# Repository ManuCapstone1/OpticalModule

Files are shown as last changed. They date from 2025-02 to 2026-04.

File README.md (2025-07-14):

# OpticalModule

This Github repository is for storing all pertinent information regarding the functionality and design of the optical module.

<p align="center">
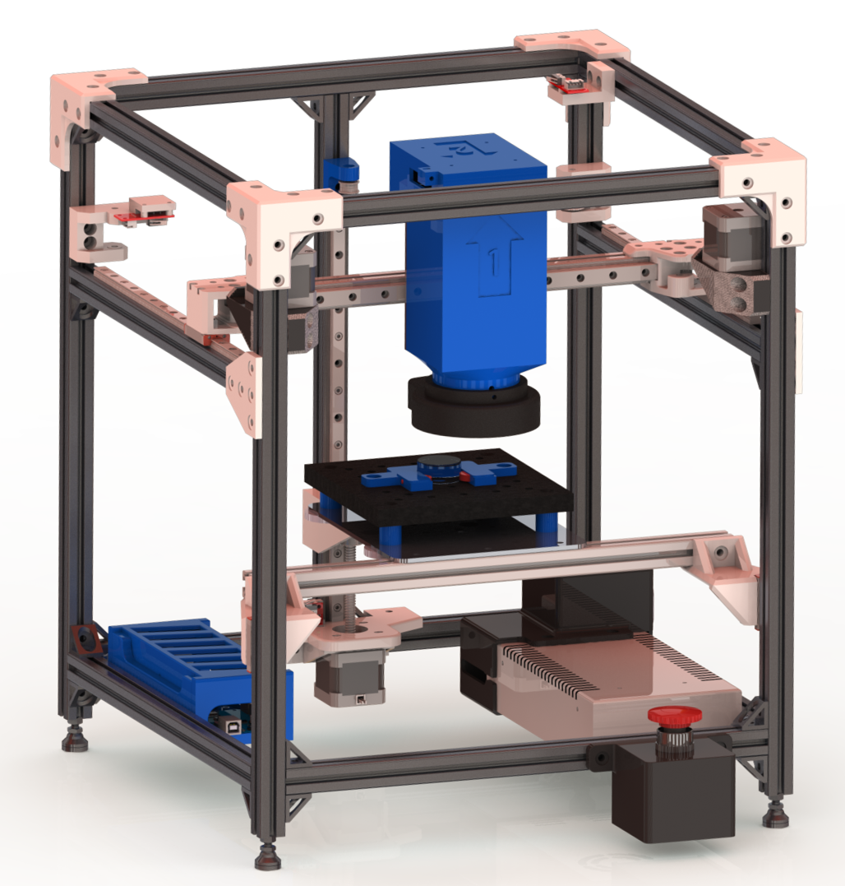
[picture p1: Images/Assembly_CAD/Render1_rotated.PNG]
  
</p>

<p align="center">
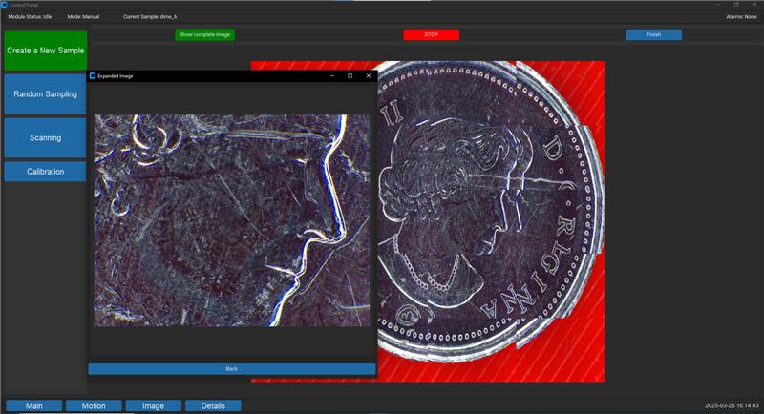
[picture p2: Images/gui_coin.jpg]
  
</p>

---

The [CAD folder](CAD/) has the full assembly of the optical module, along with files for all the 3D printed parts and engineering drawings for machined parts

The [Programming folder](Programming%20Files/) has all the programming files for the project. [pc_files](Programming%20Files/pc_files) has all python files to be run on a windows PC, to interact with the Raspberry Pi with a GUI. [module_program](Programming%20Files/module_program) has all the files to be run on the Raspberry Pi. Keep in mind that file paths are hardcoded, and would need to be modified on new devices.

[Images](Images/) holds images of various aspects of the project. Flowcharts, sample images, and images of the physical product.

[Documentation](Documentation/) lists documents relating to design, use and assembly (e.g. BOM, manual).

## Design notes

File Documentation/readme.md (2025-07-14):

## BOM
File [BOM_OpticalModule](BOM_OpticalModule.xlsx) has a list of all the parts and tools needed to create the optical module, along with links to vendors and parts.

The first sheet has the exhaustive list of all the parts. The second sheet 'Fasteners' has three seperate tables, with various grouping combination for ease of use. The third sheet has a list of all the 3D printed parts and approximate material costs. The fourth sheet has a list of all needed tools to assembly and construct the microscope.

Parts were sourced through the following vendors: Aliexpress, Amazon, piShop, and McMaster. A very rough estimate of all the costs is about $1600 CAD, excluding tax, shipping costs, and tools.

## Assembly Instructions
Instructions on how to assemble and setup all components of the optical module.

## Manual
Instructions on how to run, operate, and maintain the optical module. Does not include design decisions, or assembly instructions.

## Electrical Diagram
Fritzing file of the module's electrical setup.

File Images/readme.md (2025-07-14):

### Assembly_CAD
Rendered images of microscope in CAD from different angles and viewpoints.

### Charuco
Images of charuco board taken with the microscope during testing.

### Diagrams
Flowcharts and diagrams to explain programming structure. Referenced in readme.md file in programming folders.

### Picture
Pictures taken of the microscope from various different angles and viewpoints to assist with assembly.

### coin_stitched_example
An example of the files that would be outputted during a scanning routine of the optical module.

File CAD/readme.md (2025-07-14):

-To access the project assembly to go the "Optical Module Final Assembly" folder and download "Optical Module CAD.zip". 

-Open the "430 Main project assy" file for the final assembly.

The structure of the assmebly for this project took a lot of inspiration from rolohuan's SimpleCore 3D printer.

“rolohaun/SimpleCore: DIY CoreXY Printer called SimpleCore.” https://github.com/rolohaun/SimpleCore/tree/main (accessed Nov. 25, 2024).

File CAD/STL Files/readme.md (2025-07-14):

# 3D Printing Instructions

## Parts List
All .STL files to be 3D printed. Below is the list of all the parts and the quantity needed.
See [Download BOM.xlsx](./OpticalModule/Documentation/Github_BOM.xlsx) for a more detailed BOM.

| Part Name                | Notes                                | Quantity | Link |
|--------------------------|--------------------------------------|----------|------|
| *Enclosure Base V2       |                                      | 1        |      |
| Enclosure Cover Front    |                                      | 1        |      |
| Enclosure Cover Upper    |                                      | 1        |      |
| Belt Adapter             |                                      | 1        |      |
| Idler Mount B            |                                      | 1        |      |
| Idler Mount A            | Limit switch mount                   | 1        |      |
| **XY Motor mount         | One as is, the other mirrored.       | 2        |      |
| **Z Carriage             | One as is, the other mirrored.       | 2        |      |
| Ball Screw Bracket       |                                      | 1        |      |
| Belt Tensioner           |                                      | 1        |      |
| Z Motor bracket          |                                      | 1        |      |
| Left Y Carriage Top      |                                      | 1        | [rolohaun](https://github.com/rolohaun/SimpleCore/tree/main/CAD) | 
| Left Y Carriage Bottom   |                                      | 1        | [rolohaun](https://github.com/rolohaun/SimpleCore/tree/main/CAD) |
| Right Y Carriage Top     |                                      | 1        | [rolohaun](https://github.com/rolohaun/SimpleCore/tree/main/CAD) |
| Right Y Carriage Bottom  |                                      | 1        | [rolohaun](https://github.com/rolohaun/SimpleCore/tree/main/CAD) |
| X Limit Switch Mount     |                                      | 1        |       |
| Housing Top              |                                      | 1        |       |
| Housing Base             |                                      | 1        |       |
| estop enclosure top      |                                      | 1        |       |
| estop enclosure bottom   |                                      | 1        |       |
| Power supply housing     |                                      | 1        |       |
| Sample holder base       |                                      | 1        |       |
| Sample holder clamping plate |                                  | 2        |       |
| Sample holder pin        |   Add a spring from a pen to the cylindrical part of the pin.  | 2        |       |
| ***MGN9 Linear Rail Jig  |  Print standard/weaker settings.     | 2        | [Thingiverse](https://www.thingiverse.com/thing:5903898/files) |
| ***MGN12 Linear Rail Jig |  Print standard/weaker settings.     | 2        | [Thingiverse](https://www.thingiverse.com/thing:5903898/files) |
| T-bracket                |                                      | 4        | [Thingiverse](https://www.thingiverse.com/thing:2503622/files) |
| Top Corner Bracket       |                                      | 4        | [Thingiverse](https://www.thingiverse.com/thing:2655498) |
| Ball Screw Knob          | Scaled at 97%                        | 1        | [Thingiverse](https://www.thingiverse.com/thing:3014508/files) |
| Cable Management Clips   | File not uploaded. Select as needed. | ~10      | [Thingiverse](https://www.thingiverse.com/thing:4612080/files) |

**EnclosureBase should be printed with the supports filling in the interior of the shell.*

** *Print one as is, then print another but mirrored.*

*** *Since these parts are not apart of the ovedrall structure and used just for alignment, they can be printed on weak/low settings (e.g. infill 20%, shell thickness 0.8mm).*

## Recommended Print Settings
### Printer

Recommend using an *FDM printer*. Parts should hold good structural integrity to reduce wear and vibrations of the system.

### Material
Strong materials like ABS are the most preferred. However, PLA and PLA + are sufficient.

### Slicer Setting
The following suggestions are simply *suggestions*. If you are familiar with 3D printing, use you're discretion.

| Parameter        | Suggested Setting |
| -----------------| ----------------- |
| Resolution       | 0.02 mm           |
| Infill           | 40%-60%           |
| Infill Pattern   | Cubic             |
| Shell Thickness  | 1.2 mm            |
| Supports         | > 45 degrees. For nicer surface finish, place supports at the bottom of parts. |

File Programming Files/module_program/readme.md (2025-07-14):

# Overview
The purpose of this code is to operate the physical system. It can receive commands from the GUI and execute the requested method while publishing data on the current module status.

<p align="center">
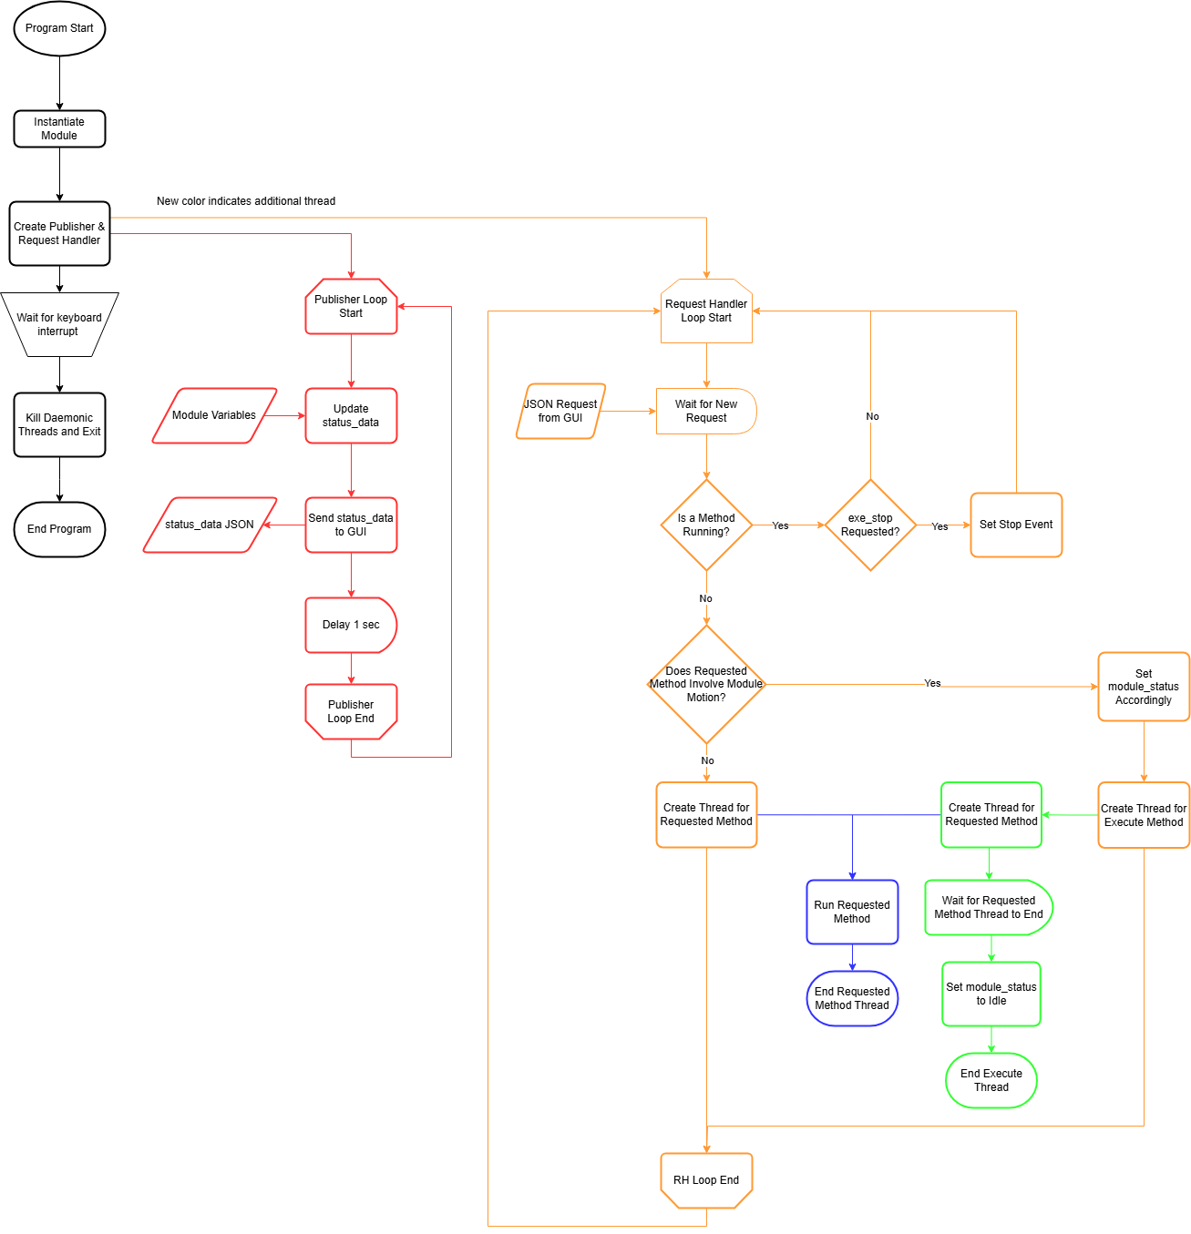
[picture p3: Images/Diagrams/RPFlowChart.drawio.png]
Raspberry Pi Program Diagram
  
</p>

---
# Files

## opticalmodule.py
This Python file contains classes that represent the physical system with methods for system operation.

## rpmain.py
This Python file handles opening and closing sockets and functions for publishing data and handling requests from the GUI.

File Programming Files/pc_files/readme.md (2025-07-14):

# Overview
The purpose of this code is to communicate user requests to the Optical module code (i.e. Raspberry Pi). User requests are handled in a Graphical User Interface (GUI).
The code is designed to be run on a Windows PC that is connected to the Raspberry Pi with an Ethernet cable.

<p align="center">
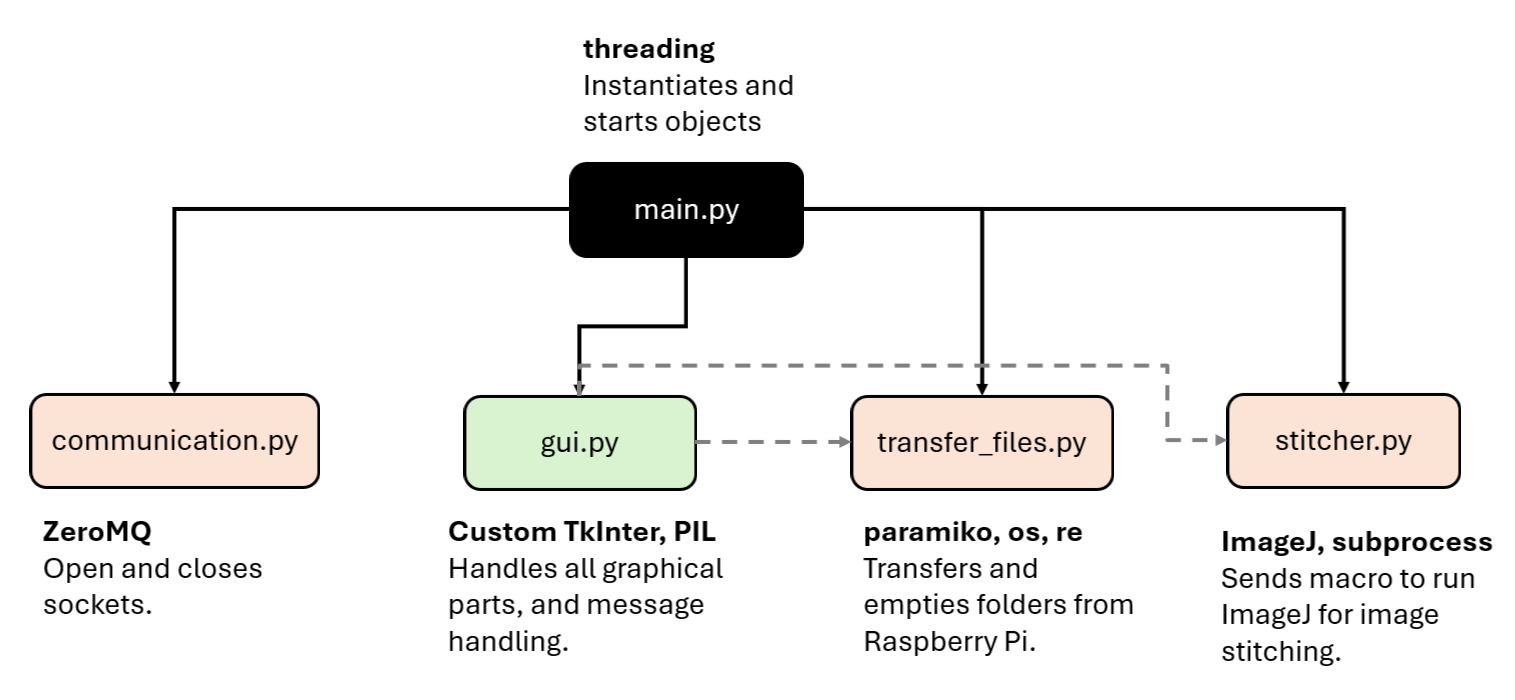
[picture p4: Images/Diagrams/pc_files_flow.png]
PC files diagram
  
</p>

---
# Files

## main.py
All the Python files for the PC, except for main, are simply classes. Main instantiates objects from the other Python files and then starts the program. It also assists with closing the sockets and the program smoothly when the GUI exits.

## communication.py
This Python file handles opening and closing sockets. The Python library to handle the sockets is ZeroMQ. There are two sockets used:

**SUB Socket**
The subscriber socket works in tandem with the Raspberry Pi's publisher socket. The Raspberry Pi sends live data to the PC every second.
This is run on a separate thread so that it can continue to get updates asynchronously.

**REQ Socket**
The request socket works in tandem with the Raspberry Pi's response socket. This is used to send JSON objects to the Raspberry Pi to detail user requests (e.g. exe_stop, number of sampling images).

**Note**
The IP address, host name, and password are hardcoded into the code. Change as needed to fit the specs of your Raspberry Pi or whichever device you use.

<p align="center">
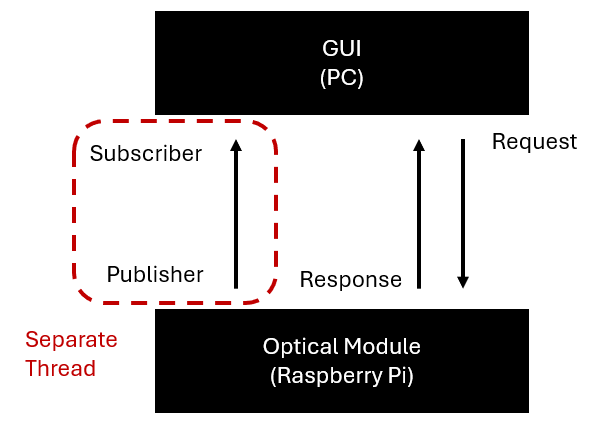
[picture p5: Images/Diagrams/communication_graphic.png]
PC files diagram
  
</p>

## stitcher.py
The stitcher program runs a macro that passes in arguments to ImageJ (i.e. FiJi). The image stitching process takes some time (up to 2 minutes). Therefore, this process is also run on a separate thread when it is called.

## transfer_files.py
Images are stored in a folder on the Raspberry Pi called "image_buffer," regardless of the process being executed. An SFTP client connection must be opened in order to transfer those files from a directory in the Raspberry Pi over to a directory in the PC. Furthermore, to empty the "image_buffer" folder, an SSH client connection is created and then closed after completion. This Python file handles all this communication and connections.

## gui.py
gui.py is basically the "main" code, as it handles all the graphical parts of the GUI, as well as uses the objects from the other files to communicate and sequence the user requests to the Raspberry Pi.
The code can be separated into three main chunks, in order of how it was written: instantiation of variables, graphical components, message handling with the Raspberry Pi.

### Instantiation
At the top of the program, many variables are instantiated. Without some of these instantiations, errors may arise as some variables are updated every second from the Raspberry Pi, but would otherwise only be instantiated if that particular screen where the variable is displayed is open.

Note that it is in this section where the folder paths are instantiated. Change these directories as needed to match your directory.

### Graphics
Most of the code is simply widgets, frames, buttons, etc. to display the GUI. Key functionality to note is that many of the buttons use functions that send data to the Raspberry Pi. For example, the section of code that programs the "Stop" button will also have the code that sends the command to the Raspberry Pi.

### Communication
This section of code includes the image transferring (i.e., using transfer_files.py), code for starting the stitching thread, and the step-by-step processes for handling scanning and sampling processes. There are two key functions I want to note:

**update_status_data**

This function is run every second on a separate thread as it is used in the CommunicationHandler object. This function is run every second, so to ensure thread safety, only unpacking JSON data should be completed here, and everything else should be completed on the main thread.

**update_gui_elements**

This function is called within the update_status_data function like so:

`self.content_frame.after(0, self.update_gui_elements)`

This ensures all actions that need to take place in response to the Raspberry Pi's live data should happen here. This is where significant updates are coded, as well as the "state machine"-like code for running scanning and sampling.
Note that anything that takes more than ~1 second will cause the code to crash, as the function is called every second. Therefore, for any functions that require more time, run that function on a separate thread. For example, this is done for stitching as well as transferring the files from the Raspberry Pi.

---
# In Progress
## Calibration Routine
The platform and camera are leveled and aligned manually. To "calibrate" the camera should return focus score at each corner of the platform to assist the user in knowing what to level/adjust.

## Starting Raspberry Pi Remotely
Currently, there is code in main.py (i.e., run_rpi_python_file function) that can successfully start the Raspberry Pi upon running main.py on the PC. However, there is not any code yet that will close the sockets on the Raspberry Pi when the GUI closes, like there is in main.py. This needs to be completed before run_rpi_python_file should be uncommented.

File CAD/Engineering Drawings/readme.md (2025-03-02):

# Engineering Drawings 

| Part Name                | Notes                     | Quantity  |
|--------------------------|---------------------------|-----------|
| 430 Main project assy    | Full assembly             | 1         |
| Enclosure Backplate      | Metal Backplate for Carriage Enclosure| 1        |
| breadboard platform      | Extra leveling holes in breadboard    | 1         |
| support platform         |                           | 1         |

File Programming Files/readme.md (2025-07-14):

### archived
Folder with old programming files. Many including test files and demos used during the software development process.

### module_program
All the programming files needed and run on the Raspberry Pi. To start the process, run rpmain.py.

### pc_files
All the programming files needed to run a GUI on a windows PC. To start the process, run main.py.

### fiji
Files and information pertaining to Fiji (ImageJ), which handles the image stitching.

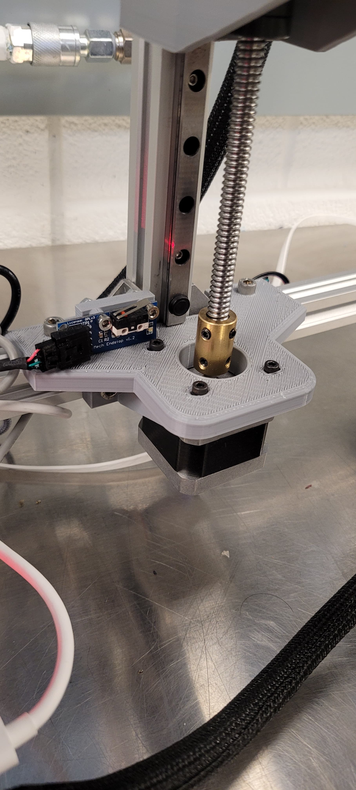
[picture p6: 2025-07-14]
Images/Picture/z_bracket.jpg

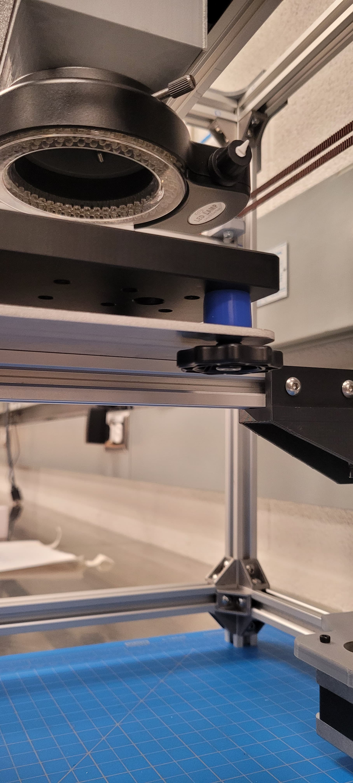
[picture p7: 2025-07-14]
Images/Picture/platform_underside.jpg

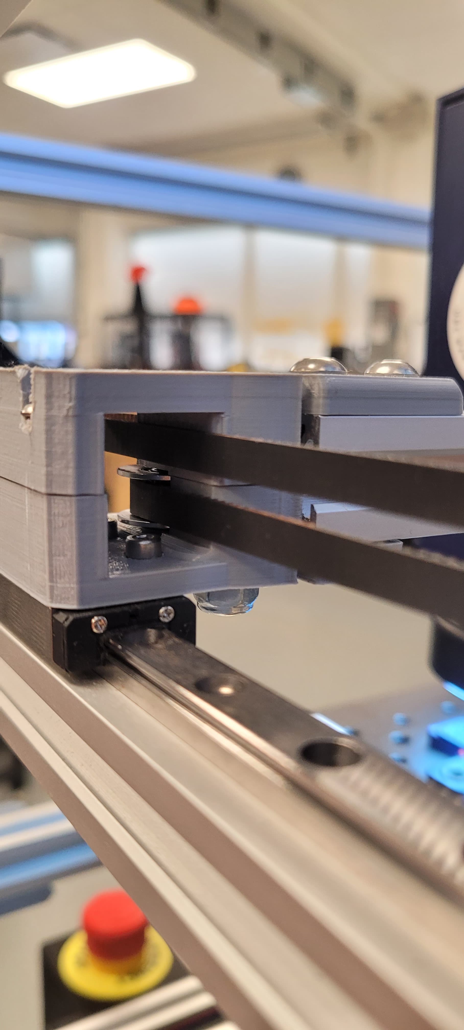
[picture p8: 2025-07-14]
Images/Picture/back_belt_right.jpg

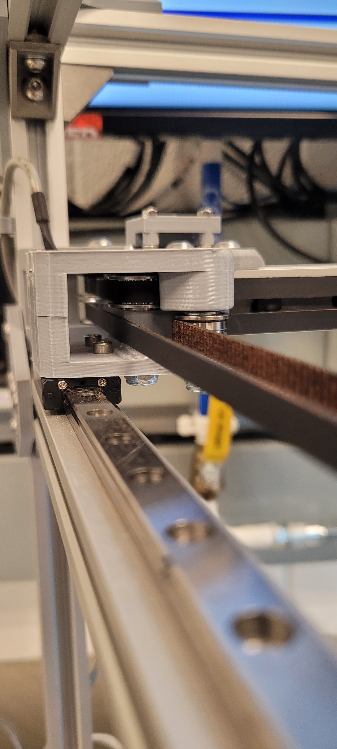
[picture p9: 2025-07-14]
Images/Picture/front_belt_left.jpg

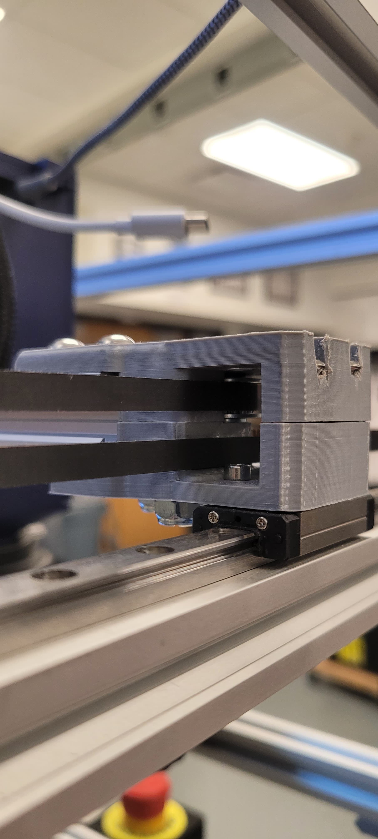
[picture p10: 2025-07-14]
Images/Picture/back_belt_left.jpg

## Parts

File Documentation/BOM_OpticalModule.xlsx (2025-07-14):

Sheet: BOM
Category | Designator | Component | Description | Number | Quanitity in Bundle | Part Cost (CAD) | Total Cost (CAD) | Part Cost (USD) | Total Cost (USD) | Vendor | Source of materials
Electrical | E1 | Arduino Uno |  | 1 | 1 | $2.45 | $2.45 | $1.79 | $1.79 | Aliexpress (https://www.aliexpress.com/item/1005007335850929.html?curPageLogUid=IXUFiCyfGnTw&utparam-url=scene%3Asearch%7Cquery_from%3A) | https://www.aliexpress.com/item/1005007335850929.html?curPageLogUid=IXUFiCyfGnTw&utparam-url=scene%3Asearch%7Cquery_from%3A
Electrical | E2 | Arduino CNC Shield V3.00 | Includes 3 drivers for motors. | 1 | 1 | $5.78 | $5.78 | $4.22 | $4.22 | Aliexpress (https://www.aliexpress.com/item/1005005995728092.html?curPageLogUid=Z2e3c3z85Mul&utparam-url=scene%3Asearch%7Cquery_from%3A) | https://www.aliexpress.com/item/1005005995728092.html?curPageLogUid=Z2e3c3z85Mul&utparam-url=scene%3Asearch%7Cquery_from%3A
Electrical | E3 | *USB-A to USB-B Cable | > 50cm long | 1 | 1 | $3.51 | $3.51 | $2.56 | $2.56 | Aliexpress (https://www.aliexpress.com/item/32700175631.html?curPageLogUid=ho6akVY6lwlr&utparam-url=scene%3Asearch%7Cquery_from%3A) | https://www.aliexpress.com/item/32700175631.html?curPageLogUid=ho6akVY6lwlr&utparam-url=scene%3Asearch%7Cquery_from%3A
Electrical | E4 | USB A 90 deg corner adapter | For plugging in USB A - USB B cable into raspberry Pi | 1 | 1 | $8.99 | $8.99 | $6.56 | $6.56 | Amazon (https://www.amazon.ca/gp/product/B0CPPFDG7M?smid=A2O45EW0W6FNOE&th=1) | https://www.amazon.ca/gp/product/B0CPPFDG7M?smid=A2O45EW0W6FNOE&th=1
Electrical | E5 | *Stepper Motor | NEMA 17, 1.8deg, 1A | 3 | 3 | $51.52 | $51.52 | $37.61 | $37.61 | Amazon (https://www.amazon.ca/STEPPERONLINE-Stepper-Bipolar-42x42x38mm-Connector/dp/B0B38GHRH8?s=industrial) | https://www.amazon.ca/STEPPERONLINE-Stepper-Bipolar-42x42x38mm-Connector/dp/B0B38GHRH8?s=industrial
Electrical | E6 | Stepper Motor Cables | 4 Pin, < 60cm long | 3 | 4 | $14.99 | $14.99 | $10.94 | $10.94 | Amazon (https://www.amazon.ca/Stepper-Printer-Connection-Printers-Machines/dp/B09CDGZ3JR?s=industrial) | https://www.amazon.ca/Stepper-Printer-Connection-Printers-Machines/dp/B09CDGZ3JR?s=industrial
Electrical | E7 | *Limit Switches | Mechanical Endstop V1.2 with Cable | 3 | 3 | $3.38 | $3.38 | $2.47 | $2.47 | Aliexpress (https://www.aliexpress.com/item/1005007505049085.html?curPageLogUid=tV7LOpvrjGV0&utparam-url=scene%3Asearch%7Cquery_from%3A) | https://www.aliexpress.com/item/1005007505049085.html?curPageLogUid=tV7LOpvrjGV0&utparam-url=scene%3Asearch%7Cquery_from%3A
Electrical | E8 | Raspberry Pi | Pi 5, RAM 2GB | 1 | 1 | $97.12 | $97.12 | $70.90 | $70.90 | piShop (https://www.pishop.ca/product/raspberry-pi-5-2gb/) | https://www.pishop.ca/product/raspberry-pi-5-2gb/
Electrical | E9 | SD Card for Raspberry Pi | Class 10, 32GB or more | 1 | 1 | $14.99 | $14.99 | $10.94 | $10.94 | Amazon (https://www.amazon.ca/dp/B074B4BFHJ?ref=ppx_yo2ov_dt_b_fed_asin_title) | https://www.amazon.ca/dp/B074B4BFHJ?ref=ppx_yo2ov_dt_b_fed_asin_title
Electrical | E10 | microHDMI Cable | Optional, for displaying Raspberry Pi to monitor. | 1 | 1 | $3.56 | $3.56 | $2.60 | $2.60 | Aliexpress (https://www.aliexpress.com/item/1005006939910638.html?curPageLogUid=pBYEOeD0V9b2&utparam-url=scene%3Asearch%7Cquery_from%3A) | https://www.aliexpress.com/item/1005006939910638.html?curPageLogUid=pBYEOeD0V9b2&utparam-url=scene%3Asearch%7Cquery_from%3A
Electrical | E11 | Ethernet Cable | 90 degree corner facing upwards, cable in direction of locking tab | 1 | 1 | $16.99 | $16.99 | $12.40 | $12.40 | Amazon (https://www.amazon.ca/Ethernet-Downward-Gigabit-Internet-Network/dp/B0CPP6JCD4?s=industrial) | https://www.amazon.ca/Ethernet-Downward-Gigabit-Internet-Network/dp/B0CPP6JCD4?s=industrial
Electrical | E12 | *USB C to USB C Cable | >40cm long | 1 | 1 | $2.90 | $2.90 | $2.12 | $2.12 | Aliexpress (https://www.aliexpress.com/item/1005006837967970.html?curPageLogUid=HkNTrdvCsyI1&utparam-url=scene%3Asearch%7Cquery_from%3A) | https://www.aliexpress.com/item/1005006837967970.html?curPageLogUid=HkNTrdvCsyI1&utparam-url=scene%3Asearch%7Cquery_from%3A
Electrical | E13 | USB C Female Breakout Board PCB | For powering Raspberry Pi from power supply. | 1 | 1 | $4.39 | $4.39 | $3.20 | $3.20 | Aliexpress (https://www.aliexpress.com/item/1005007382623157.html?curPageLogUid=2fLlCee037Sf&utparam-url=scene%3Asearch%7Cquery_from%3A) | https://www.aliexpress.com/item/1005007382623157.html?curPageLogUid=2fLlCee037Sf&utparam-url=scene%3Asearch%7Cquery_from%3A
Electrical | E14 | DC-DC Step Down Buck Converter Module | LM2596 | 3 | 4 | $12.99 | $12.99 | $9.48 | $9.48 | Amazon (https://www.amazon.ca/D-FLIFE-Converter-Adjustable-Efficiency-Transformer/dp/B0BXP5S4Q9?s=electronics) | https://www.amazon.ca/D-FLIFE-Converter-Adjustable-Efficiency-Transformer/dp/B0BXP5S4Q9?s=electronics
Electrical | E15 | *22 AWG Solid-Core Insulated Wires | For wiring Step Down Converters. >40 cm long. | 1 | 1 | $2.40 | $2.40 | $1.75 | $1.75 | Aliexpress (https://www.aliexpress.com/item/1005006106330815.html?curPageLogUid=gBPqtjxeL35T&utparam-url=scene%3Asearch%7Cquery_from%3A) | https://www.aliexpress.com/item/1005006106330815.html?curPageLogUid=gBPqtjxeL35T&utparam-url=scene%3Asearch%7Cquery_from%3A
Electrical | E16 | *Crimp Terminal Kit | Has ring and spade terminals. | 10 | 300 | $11.89 | $11.89 | $8.68 | $8.68 | Aliexpress (https://www.aliexpress.com/item/1005006856633108.html?curPageLogUid=BPyWPyZS8Sck&utparam-url=scene%3Asearch%7Cquery_from%3A) | https://www.aliexpress.com/item/1005006856633108.html?curPageLogUid=BPyWPyZS8Sck&utparam-url=scene%3Asearch%7Cquery_from%3A
Electrical | E17 | *DC Power Supply | 24VDC, ~15A, 50/60Hz | 1 | 1 | $24.16 | $24.16 | $17.64 | $17.64 | Aliexpress (https://www.aliexpress.com/item/4001127313192.html?curPageLogUid=JBaFZMyAFHxf&utparam-url=scene%3Asearch%7Cquery_from%3A) | https://www.aliexpress.com/item/4001127313192.html?curPageLogUid=JBaFZMyAFHxf&utparam-url=scene%3Asearch%7Cquery_from%3A
Electrical | E18 | *Power Inlet | 250V, 15A | 1 | 1 | $17.99 | $17.99 | $13.13 | $13.13 | Amazon (https://www.amazon.ca/3Dman-Rocker-Switch-Socket-Module/dp/B07RRY5MYZ) | https://www.amazon.ca/3Dman-Rocker-Switch-Socket-Module/dp/B07RRY5MYZ
Electrical | E19 | E-Stop | Twist release, terminal blocks, NC. 600V and 10A. | 1 | 1 | $17.69 | $17.69 | $12.91 | $12.91 | Amazon (https://www.amazon.ca/gp/product/B0CXJJXCPZ?smid=A13WDQ0MMLFME4&psc=1) | https://www.amazon.ca/gp/product/B0CXJJXCPZ?smid=A13WDQ0MMLFME4&psc=1
Electrical | E20 | *12 AWG Silicone Copper Wires | For wiring power supply to rocker. >60 cm long. | 1 | 1 | $4.89 | $4.89 | $3.57 | $3.57 | Aliexpress (https://www.aliexpress.com/item/1005006566120439.html?curPageLogUid=v5gUU3oau6qD&utparam-url=scene%3Asearch%7Cquery_from%3A) | https://www.aliexpress.com/item/1005006566120439.html?curPageLogUid=v5gUU3oau6qD&utparam-url=scene%3Asearch%7Cquery_from%3A
Electrical | E21 | Cable Mesh Sleeve | >1 m, > 3/8" | 1 | 1 | $13.99 | $13.99 | $10.21 | $10.21 | Amazon (https://www.amazon.ca/Alex-Tech-10ft-Protector-Sleeving/dp/B07FVZLCQY) | https://www.amazon.ca/Alex-Tech-10ft-Protector-Sleeving/dp/B07FVZLCQY
Electrical | E22 | *Cable Ties | For cable management, use as needed. | 5 | 100 | $2.59 | $2.59 | $1.89 | $1.89 | Aliexpress (https://www.aliexpress.com/item/1005007615502103.html?curPageLogUid=Gt0wmJ3Ja8vx&utparam-url=scene%3Asearch%7Cquery_from%3A) | https://www.aliexpress.com/item/1005007615502103.html?curPageLogUid=Gt0wmJ3Ja8vx&utparam-url=scene%3Asearch%7Cquery_from%3A
Electrical | E23 | *PC | Ethernet Port. Interfaces with Raspberry Pi, storage for images. Runs Windows. Prices vary significantly. | 1 |  |  | $0.00 | $0.00 | $0.00
Mechanical | M1 | Ball Screw and Nut | 150 mm long, M8, 2mm per turn. Part number: 6624K67 | 1 | 1 | $346.97 | $346.97 | $253.29 | $253.29 | McMaster Carr (https://www.mcmaster.com/6624K67/) | https://www.mcmaster.com/6624k67/
Mechanical | M2 | Coupler (motor to balls screw) | 5mm to 8mm | 1 | 1 | $2.79 | $2.79 | $2.04 | $2.04 | Aliexpress (https://www.aliexpress.com/item/1005007559926991.html?curPageLogUid=h9UFG6kcgIO0&utparam-url=scene%3Asearch%7Cquery_from%3A) | https://www.aliexpress.com/item/1005007559926991.html?curPageLogUid=h9UFG6kcgIO0&utparam-url=scene%3Asearch%7Cquery_from%3A
Mechanical | M3 | Lubricant | PTFE Dry lubricant or Superlube | 1 | 1 | $16.49 | $16.49 | $12.04 | $12.04 | Amazon (https://www.amazon.ca/WD-40%C2%AE-Specialist-Lube-PTFE-Spray/dp/B07PNK728T) | https://www.amazon.ca/WD-40%C2%AE-Specialist-Lube-PTFE-Spray/dp/B07PNK728T
Mechanical | M4 | Timing Belt | GT2, 6mm wide, > 2m long | 1 | 1 | $4.21 | $4.21 | $3.07 | $3.07 | Aliexpress (https://www.aliexpress.com/item/1005005216868552.html?curPageLogUid=aeeP4WQW6cRl&utparam-url=scene%3Asearch%7Cquery_from%3A) | https://www.aliexpress.com/item/1005005216868552.html?curPageLogUid=aeeP4WQW6cRl&utparam-url=scene%3Asearch%7Cquery_from%3A
Mechanical | M5 | Belt Pulley Toothed | GT2, 5mm bore, 6mm, toothed | 2 | 5 | $9.99 | $9.99 | $7.29 | $7.29 | Amazon (https://www.amazon.ca/Saiper-Aluminum-Synchronous-Compatible-Printer/dp/B07M9W6K2W) | https://www.amazon.ca/Saiper-Aluminum-Synchronous-Compatible-Printer/dp/B07M9W6K2W
Mechanical | M6 | Pulley Idler Toothed | GT2, 5mm bore, 6mm, toothed idler | 6 | 10 | $18.98 | $18.98 | $13.86 | $13.86 | Amazon (https://www.amazon.ca/BZ-3D-Pulley-Printer-Timing/dp/B0CX923N61) | https://www.amazon.ca/BZ-3D-Pulley-Printer-Timing/dp/B0CX923N61
Mechanical | M7 | Bearings | F695-2RS, 5x13x4mm, flanged | 8 | 20 | $20.39 | $20.39 | $14.88 | $14.88 | Amazon (https://www.amazon.ca/uxcell-F695-2RS-Flanged-5x13x4mm-Bearings/dp/B0CGXF48ZZ) | https://www.amazon.ca/uxcell-F695-2RS-Flanged-5x13x4mm-Bearings/dp/B0CGXF48ZZ
Mechanical | M8 | *PLA, PLA +, ABS | Spool (1kg) | 2 | 1 | $24.99 | $49.98 | $18.24 | $36.49 | Amazon (https://www.amazon.ca/DURAMIC-3D-Filament-Printing-Dimensional/dp/B07TW9KTVV) | https://www.amazon.ca/DURAMIC-3D-Filament-Printing-Dimensional/dp/B07TW9KTVV
Machined | M9 | Enclosure Backplate | 105x80x5mm. See engineering drawing | 1 | 1 | $7.34 | $7.34 | $5.36 | $5.36 | Aliexpress (https://www.aliexpress.com/item/1005002064688784.html?curPageLogUid=5C4xniOMl7Jm&utparam-url=scene%3Asearch%7Cquery_from%3A) | https://www.aliexpress.com/item/1005002064688784.html?curPageLogUid=5C4xniOMl7Jm&utparam-url=scene%3Asearch%7Cquery_from%3A
Machined | M10 | *Mounting plate for stage | 150x185x4mm. See engineering drawing. | 1 | 1 | $22.30 | $22.30 | $16.28 | $16.28 | Aliexpress (https://www.aliexpress.com/item/1005008534675427.html?curPageLogUid=kxY6Z8TX34Pc&utparam-url=scene%3Asearch%7Cquery_from%3A) | https://www.aliexpress.com/item/1005008534675427.html?curPageLogUid=kxY6Z8TX34Pc&utparam-url=scene%3Asearch%7Cquery_from%3A
Mechanical | M11 | Spacers and Knobs for Stage | Package of 4 spacers and knobs, M4 fastener, and knobs. Typically used for 3D printers. | 1 | 1 | $6.19 | $6.19 | $4.52 | $4.52 | Aliexpress (https://www.aliexpress.com/item/1005006950333527.html?curPageLogUid=f3mkEXFbB0BQ&utparam-url=scene%3Asearch%7Cquery_from%3A) | https://www.aliexpress.com/item/1005006950333527.html?curPageLogUid=f3mkEXFbB0BQ&utparam-url=scene%3Asearch%7Cquery_from%3A
Machined | M12 | Breadboard Stage | 150x150x13mm | 1 | 1 | $83.68 | $83.68 | $61.09 | $61.09 | Aliexpress (https://www.aliexpress.com/item/1005006895797933.html?curPageLogUid=qSWfg5B0oj7o&utparam-url=scene%3Asearch%7Cquery_from%3A) | https://www.aliexpress.com/item/1005006895797933.html?curPageLogUid=qSWfg5B0oj7o&utparam-url=scene%3Asearch%7Cquery_from%3A
Mechanical | M13 | Bubble gage | Optional, for assistance with leveling during assembly. | 1 | 2 | $3.90 | $3.90 | $2.85 | $2.85 | Aliexpress (https://www.aliexpress.com/item/1005004129181790.html?curPageLogUid=gtLJyxTGkdct&utparam-url=scene%3Asearch%7Cquery_from%3A) | https://www.aliexpress.com/item/1005004129181790.html?curPageLogUid=gtLJyxTGkdct&utparam-url=scene%3Asearch%7Cquery_from%3A
Mechanical | M14 | Linear rail X | MGN12H 300mm | 1 | 1 | $27.55 | $27.55 | $20.11 | $20.11 | Amazon (https://www.amazon.ca/uxcell-Sliding-Carriage-Bearing-Printers/dp/B0D54L3X3Z) | https://www.amazon.ca/uxcell-Sliding-Carriage-Bearing-Printers/dp/B0D54L3X3Z
Mechanical | M15 | Linear rails Y | MGN9H 200mm | 2 | 1 | $16.99 | $33.98 | $12.40 | $24.81 | Aliexpress (https://www.aliexpress.com/item/1005008925563990.html?curPageLogUid=LjGkK1HxD36e&utparam-url=scene%3Asearch%7Cquery_from%3A) | https://www.aliexpress.com/item/1005008925563990.html?curPageLogUid=LjGkK1HxD36e&utparam-url=scene%3Asearch%7Cquery_from%3A
Mechanical | M16 | Linear Rails Z | MGN9H 300mm | 3 | 1 | $19.78 | $59.34 | $14.44 | $43.32 | Aliexpress (https://www.aliexpress.com/item/1005008925563990.html?curPageLogUid=LjGkK1HxD36e&utparam-url=scene%3Asearch%7Cquery_from%3A) | https://www.aliexpress.com/item/1005008925563990.html?curPageLogUid=LjGkK1HxD36e&utparam-url=scene%3Asearch%7Cquery_from%3A
Machined | M17 | 2020 V-Slot Aluminum Extrusion | 370mm x 11 465mm x4 395mm x1 330mm x1 255mm x1 | 1 | 1 | $129.99 | $129.99 | $94.89 | $94.89 | Amazon (https://www.amazon.ca/Aluminum-Extrusion-European-Standard-Industrial/dp/B09Y1RBCDJ?s=industrial) | https://www.amazon.ca/Aluminum-Extrusion-European-Standard-Industrial/dp/B09Y1RBCDJ?s=industrial
Mechanical | M18 | 2020 Corner Bracket |  | 34 | 20 | $8.78 | $17.56 | $6.41 | $12.82 | Aliexpress (https://www.aliexpress.com/item/1005007188219353.html?scm_id=1007.40050.354490.0&scm-url=1007.40050.354490.0) | https://www.aliexpress.com/item/1005007188219353.html?scm_id=1007.40050.354490.0&scm-url=1007.40050.354490.0
Mechanical | M19 | Leveling Feet | Adjustable height, max M6 screws, dampening | 4 | 1 | $9.33 | $37.32 | $6.81 | $27.24 | McMaster Carr (https://www.mcmaster.com/5537T982/) | https://www.mcmaster.com/5537T982/
Optical | O1 | Camera | Raspberry Pi HQ Camera CS 12.3 MP | 1 | 1 | $98.86 | $98.86 | $72.17 | $72.17 | piShop (https://www.pishop.ca/product/raspberry-pi-hq-camera-cs/) | https://www.pishop.ca/product/raspberry-pi-hq-camera-cs/
Optical | O2 | Lens | 100X Industrial Microscope Lens, C/CS-Mount, 0.12X ~ 1.8X | 1 | 1 | $47.25 | $47.25 | $34.49 | $34.49 | piShop (https://www.pishop.ca/product/100x-industrial-microscope-lens-c-cs-mount-compatible-with-raspberry-pi-hq-camera-cs/) | https://www.pishop.ca/product/100x-industrial-microscope-lens-c-cs-mount-compatible-with-raspberry-pi-hq-camera-cs/
Optical | O3 | Ring Light | 62.5mm inside, 92.5mm outside diameter. | 1 | 1 | $32.39 | $32.39 | $23.64 | $23.64 | Amazon (https://www.amazon.ca/Vision-Scientific-VMLIFR-09B-Adjustable-Illuminator/dp/B07VR2LJJL) | https://www.amazon.ca/Vision-Scientific-VMLIFR-09B-Adjustable-Illuminator/dp/B07VR2LJJL
Fastener |  | 1/4" Washer | Part number: 91081A127 | 2 | 100 | $3.51 | $3.51 | $2.56 | $2.56 | McMaster Carr (https://www.mcmaster.com/91081A127/) | https://www.mcmaster.com/91081A127/
Fastener |  | 1/4-20 x 1/2" BHCP or SHCP | Part number: 92949A537 | 1 | 50 | $9.58 | $9.58 | $6.99 | $6.99 | McMaster Carr (https://www.mcmaster.com/products/screws/drive-style~hex/length~1-2-2/length~0-500/length~0-5/system-of-measurement~inch/thread-size~1-4-20/fastener-head-type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) | https://www.mcmaster.com/products/screws/drive-style~hex/length~1-2-2/length~0-500/length~0-5/system-of-measurement~inch/thread-size~1-4-20/fastener-head-type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
Fastener |  | M2.5 Hex Nut | Purchase kit with M2.5 nuts and various M2.5 screws. See vendor link. | 20 | 120 | $20.29 | $20.29 | $14.81 | $14.81 | Amazon (https://www.amazon.ca/DTGN-300Pcs-Socket-Screws-Stainless/dp/B0CRB2LWP1) | https://www.amazon.ca/DTGN-300Pcs-Socket-Screws-Stainless/dp/B0CRB2LWP1
Fastener |  | M2.5x14 BHCP or SHCP | From kit with M2.5 nuts and various M2.5 screws. | 16 | 20 | $0.00 | $0.00 | $0.00 | $0.00 | Amazon (https://www.amazon.ca/DTGN-300Pcs-Socket-Screws-Stainless/dp/B0CRB2LWP1) | https://www.amazon.ca/DTGN-300Pcs-Socket-Screws-Stainless/dp/B0CRB2LWP1
Fastener |  | M2.5x16 FHCP | From kit with M2.5 nuts and various M2.5 screws. | 4 | 20 | $0.00 | $0.00 | $0.00 | $0.00 | Amazon (https://www.amazon.ca/DTGN-300Pcs-Socket-Screws-Stainless/dp/B0CRB2LWP1) | https://www.amazon.ca/DTGN-300Pcs-Socket-Screws-Stainless/dp/B0CRB2LWP1
Fastener |  | M3 Drop T-nut |  | 34 | 50 | $2.78 | $2.78 | $2.03 | $2.03 | Aliexpress (https://www.aliexpress.com/item/32814359094.html?curPageLogUid=ZzV9IGFvWPaL&utparam-url=scene%3Asearch%7Cquery_from%3A) | https://www.aliexpress.com/item/32814359094.html?curPageLogUid=ZzV9IGFvWPaL&utparam-url=scene%3Asearch%7Cquery_from%3A
Fastener |  | M3 Hex Nut |  | 10 | 50 | $1.62 | $1.62 | $1.18 | $1.18 | Aliexpress (https://www.aliexpress.com/item/1005007593861199.html?curPageLogUid=c6igKLlfHNfy&utparam-url=scene%3Asearch%7Cquery_from%3A) | https://www.aliexpress.com/item/1005007593861199.html?curPageLogUid=c6igKLlfHNfy&utparam-url=scene%3Asearch%7Cquery_from%3A
Fastener |  | M3x4 BHCP or SHCP |  | 4 | 50 | $1.66 | $1.66 | $1.21 | $1.21 | Aliexpress (https://www.aliexpress.com/item/32810872544.html?curPageLogUid=ru9EbACdoUoQ&utparam-url=scene%3Asearch%7Cquery_from%3A) | https://www.aliexpress.com/item/32810872544.html?curPageLogUid=ru9EbACdoUoQ&utparam-url=scene%3Asearch%7Cquery_from%3A
Fastener |  | M3x8 BHCP or SHCP |  | 16 | 50 | $2.18 | $2.18 | $1.59 | $1.59 | Aliexpress (https://www.aliexpress.com/item/32810872544.html?curPageLogUid=ru9EbACdoUoQ&utparam-url=scene%3Asearch%7Cquery_from%3A) | https://www.aliexpress.com/item/32810872544.html?curPageLogUid=ru9EbACdoUoQ&utparam-url=scene%3Asearch%7Cquery_from%3A
Fastener |  | M3x8 SHCP |  | 34 | 50 | $2.18 | $2.18 | $1.59 | $1.59 | Aliexpress (https://www.aliexpress.com/item/32810872544.html?curPageLogUid=ru9EbACdoUoQ&utparam-url=scene%3Asearch%7Cquery_from%3A) | https://www.aliexpress.com/item/32810872544.html?curPageLogUid=ru9EbACdoUoQ&utparam-url=scene%3Asearch%7Cquery_from%3A
Fastener |  | M3x12 BHCP or SHCP |  | 18 | 50 | $2.63 | $2.63 | $1.92 | $1.92 | Aliexpress (https://www.aliexpress.com/item/32810872544.html?curPageLogUid=ru9EbACdoUoQ&utparam-url=scene%3Asearch%7Cquery_from%3A) | https://www.aliexpress.com/item/32810872544.html?curPageLogUid=ru9EbACdoUoQ&utparam-url=scene%3Asearch%7Cquery_from%3A
Fastener |  | M3x16 BHCP or SHCP |  | 4 | 50 | $3.10 | $3.10 | $2.26 | $2.26 | Aliexpress (https://www.aliexpress.com/item/32810872544.html?curPageLogUid=ru9EbACdoUoQ&utparam-url=scene%3Asearch%7Cquery_from%3A) | https://www.aliexpress.com/item/32810872544.html?curPageLogUid=ru9EbACdoUoQ&utparam-url=scene%3Asearch%7Cquery_from%3A
Fastener |  | M3x30 BHCP or SHCP |  | 4 | 50 | $4.12 | $4.12 | $3.01 | $3.01 | Aliexpress (https://www.aliexpress.com/item/32810872544.html?curPageLogUid=ru9EbACdoUoQ&utparam-url=scene%3Asearch%7Cquery_from%3A) | https://www.aliexpress.com/item/32810872544.html?curPageLogUid=ru9EbACdoUoQ&utparam-url=scene%3Asearch%7Cquery_from%3A
Fastener |  | M4 Hex Nut |  | 2 | 25 | $1.46 | $1.46 | $1.07 | $1.07 | Aliexpress (https://www.aliexpress.com/item/1005007593861199.html?curPageLogUid=c6igKLlfHNfy&utparam-url=scene%3Asearch%7Cquery_from%3A) | https://www.aliexpress.com/item/1005007593861199.html?curPageLogUid=c6igKLlfHNfy&utparam-url=scene%3Asearch%7Cquery_from%3A
Fastener |  | M4x14 BHCP or SHCP |  | 2 | 20 | $2.61 | $2.61 | $1.91 | $1.91 | Aliexpress (https://www.aliexpress.com/item/32810872544.html?curPageLogUid=ru9EbACdoUoQ&utparam-url=scene%3Asearch%7Cquery_from%3A) | https://www.aliexpress.com/item/32810872544.html?curPageLogUid=ru9EbACdoUoQ&utparam-url=scene%3Asearch%7Cquery_from%3A
Fastener |  | M5 Drop T-Nut |  | 168 | 100 | $5.52 | $11.04 | $4.03 | $8.06 | Aliexpress (https://www.aliexpress.com/item/32814359094.html?curPageLogUid=ZzV9IGFvWPaL&utparam-url=scene%3Asearch%7Cquery_from%3A) | https://www.aliexpress.com/item/32814359094.html?curPageLogUid=ZzV9IGFvWPaL&utparam-url=scene%3Asearch%7Cquery_from%3A
Fastener |  | M5 Hex Nut |  | 12 | 50 | $1.87 | $1.87 | $1.37 | $1.37 | Aliexpress (https://www.aliexpress.com/item/1005007593861199.html?curPageLogUid=c6igKLlfHNfy&utparam-url=scene%3Asearch%7Cquery_from%3A) | https://www.aliexpress.com/item/1005007593861199.html?curPageLogUid=c6igKLlfHNfy&utparam-url=scene%3Asearch%7Cquery_from%3A
Fastener |  | M5 Washers |  | 74 | 100 | $1.94 | $1.94 | $1.42 | $1.42 | Aliexpress (https://www.aliexpress.com/item/4000174460068.html?curPageLogUid=huSKDWt2zD75&utparam-url=scene%3Asearch%7Cquery_from%3A) | https://www.aliexpress.com/item/4000174460068.html?curPageLogUid=huSKDWt2zD75&utparam-url=scene%3Asearch%7Cquery_from%3A
Fastener |  | M5x10 BHCP |  | 168 | 100 | $14.86 | $29.72 | $10.85 | $21.70 | Amazon (https://www.amazon.ca/iexcell-Stainless-Socket-Button-Screws/dp/B0BJVNYWW1) | https://www.amazon.ca/iexcell-Stainless-Socket-Button-Screws/dp/B0BJVNYWW1
Fastener |  | M5x40 BHCP or SHCP |  | 2 | 10 | $4.15 | $4.15 | $3.03 | $3.03 | Aliexpress (https://www.aliexpress.com/item/32810872544.html?curPageLogUid=ru9EbACdoUoQ&utparam-url=scene%3Asearch%7Cquery_from%3A) | https://www.aliexpress.com/item/32810872544.html?curPageLogUid=ru9EbACdoUoQ&utparam-url=scene%3Asearch%7Cquery_from%3A
Fastener |  | M5x40 SHCP |  | 8 | 10 | $0.00 | $0.00 | $0.00 | $0.00 | Aliexpress (https://www.aliexpress.com/item/32810872544.html?curPageLogUid=ru9EbACdoUoQ&utparam-url=scene%3Asearch%7Cquery_from%3A) | https://www.aliexpress.com/item/32810872544.html?curPageLogUid=ru9EbACdoUoQ&utparam-url=scene%3Asearch%7Cquery_from%3A
Fastener |  | M5x45 BHCP or SHCP |  | 1 | 10 | $4.70 | $4.70 | $3.43 | $3.43 | Aliexpress (https://www.aliexpress.com/item/32810872544.html?curPageLogUid=ru9EbACdoUoQ&utparam-url=scene%3Asearch%7Cquery_from%3A) | https://www.aliexpress.com/item/32810872544.html?curPageLogUid=ru9EbACdoUoQ&utparam-url=scene%3Asearch%7Cquery_from%3A
Fastener |  | M6x14 BHCP or SHCP |  | 2 | 10 | $3.02 | $3.02 | $2.20 | $2.20 | Aliexpress (https://www.aliexpress.com/item/32810872544.html?curPageLogUid=ru9EbACdoUoQ&utparam-url=scene%3Asearch%7Cquery_from%3A) | https://www.aliexpress.com/item/32810872544.html?curPageLogUid=ru9EbACdoUoQ&utparam-url=scene%3Asearch%7Cquery_from%3A
Total |  |  |  |  |  |  | $1530.76 |  | $1117.46
*Was not purchased, but scrapped elsewhere. Listed vendor and link provide example part.
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

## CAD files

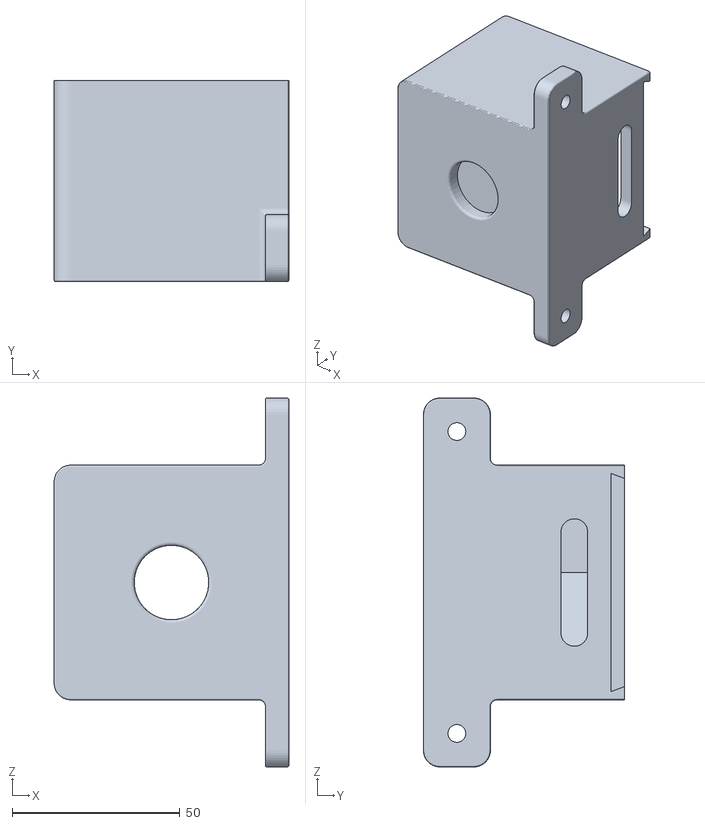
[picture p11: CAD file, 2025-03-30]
CAD/STL Files/estop enclosure top 1.STL
70.0 x 60.0 x 110.0

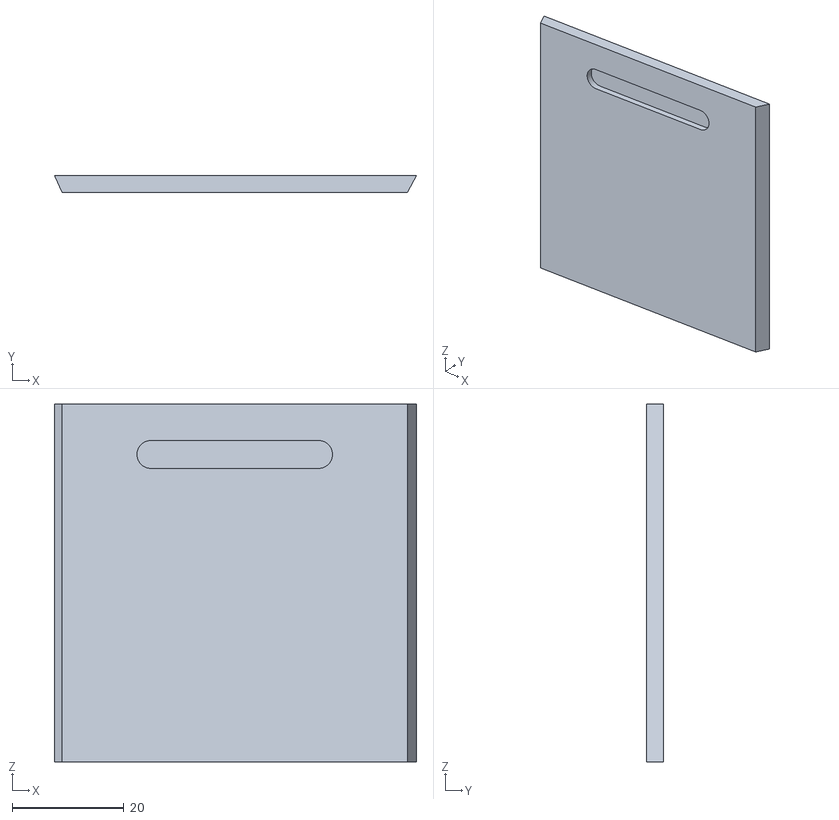
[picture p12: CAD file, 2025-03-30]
CAD/STL Files/estop enclosure bottom 1.STL
64.8 x 3.00 x 64.0

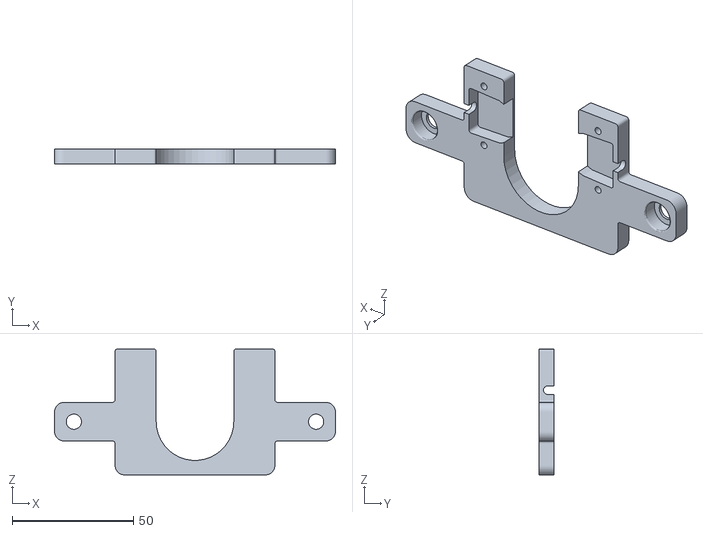
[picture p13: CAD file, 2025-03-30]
CAD/STL Files/sample holder base 1.STL
116.0 x 6.00 x 52.0

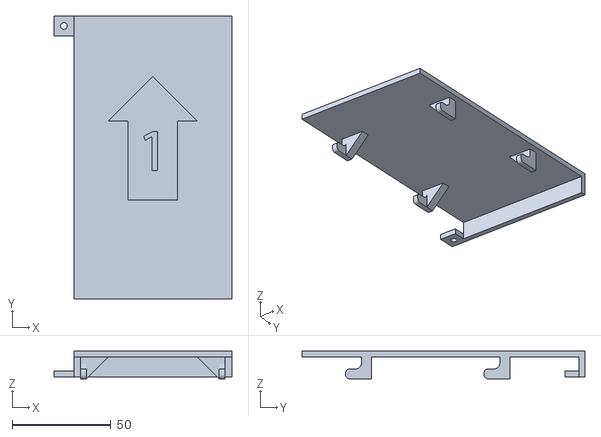
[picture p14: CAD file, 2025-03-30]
CAD/STL Files/EnclosureCoverFront.STL
90.0 x 143.0 x 14.0

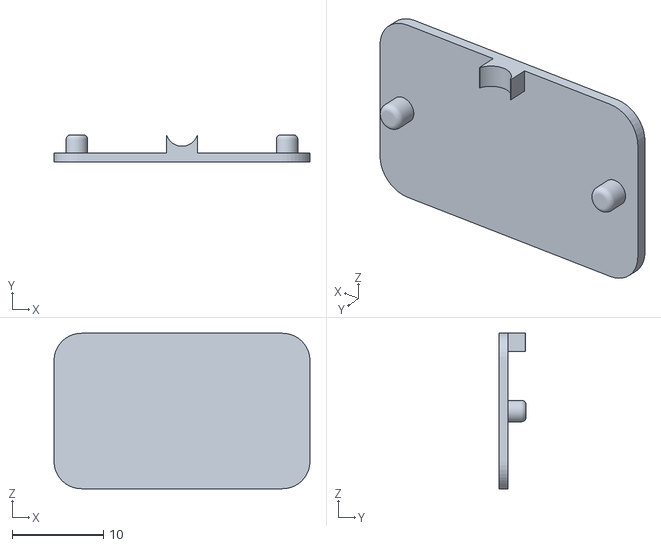
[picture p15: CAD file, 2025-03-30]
CAD/STL Files/sample holer clamping plate 1.STL
28.0 x 3.00 x 17.0

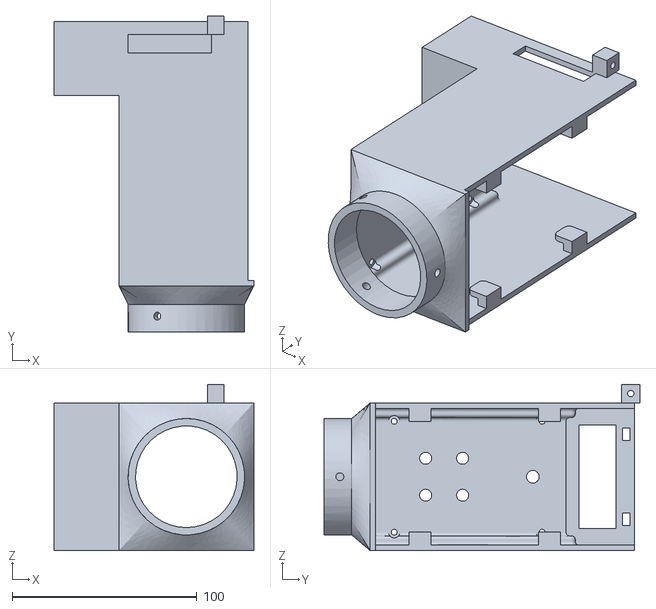
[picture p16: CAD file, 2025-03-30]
CAD/STL Files/EnclosureBaseV2.STL
108.0 x 171.0 x 90.0

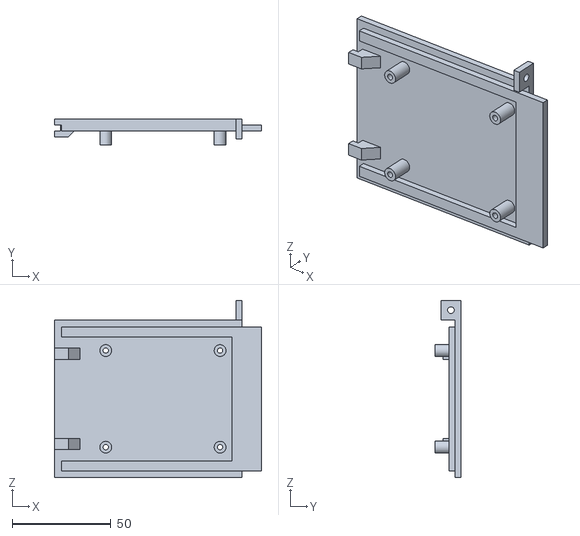
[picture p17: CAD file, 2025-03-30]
CAD/STL Files/EnclosureCoverUpper.STL
105.0 x 13.0 x 90.0

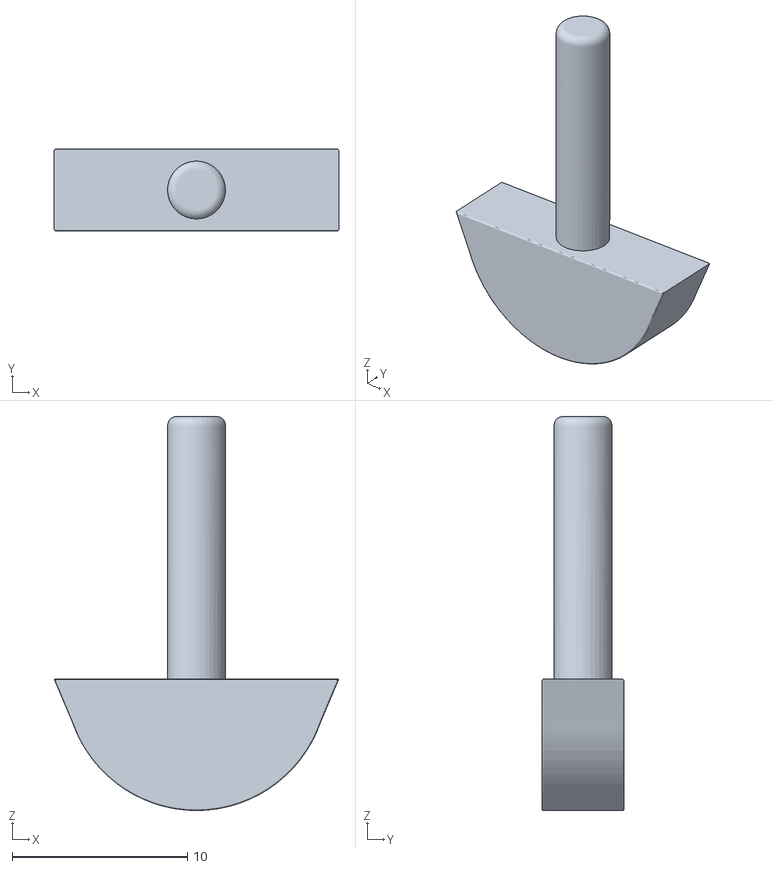
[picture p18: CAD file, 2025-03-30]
CAD/STL Files/sample holder pin 1.STL
16.2 x 4.70 x 22.5

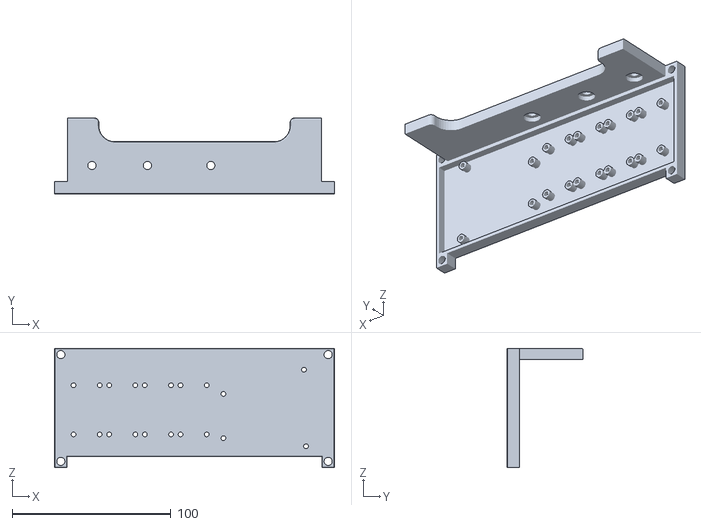
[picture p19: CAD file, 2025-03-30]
CAD/STL Files/Housing_base 1.STL
176.6 x 48.0 x 75.3

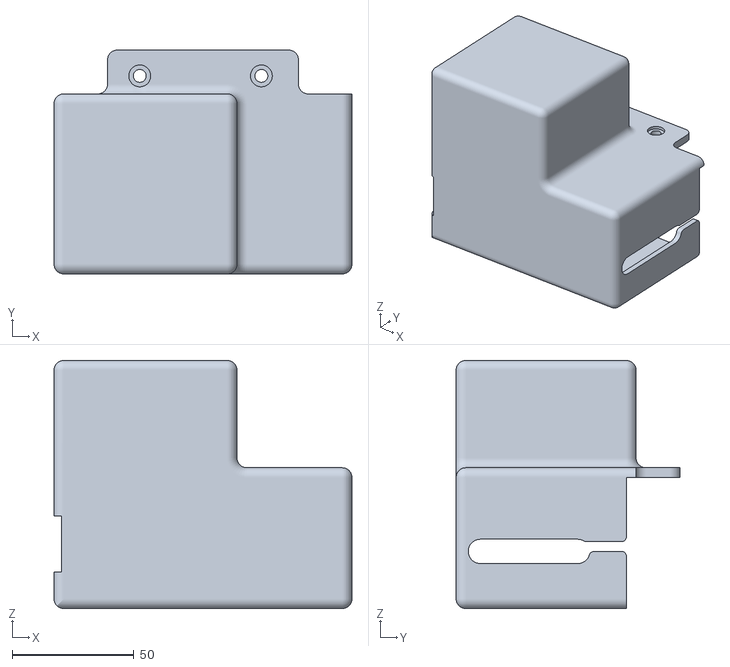
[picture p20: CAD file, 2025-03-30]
CAD/STL Files/power supply housing 1.STL
122.5 x 92.0 x 102.0

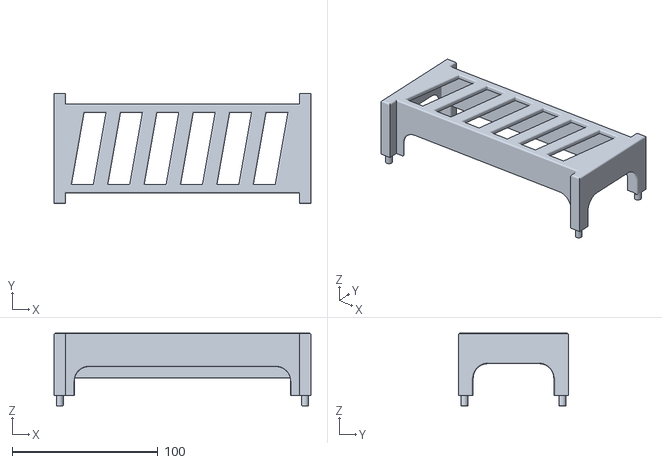
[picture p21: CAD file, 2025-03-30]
CAD/STL Files/Housing_top 2.STL
176.6 x 75.3 x 50.0

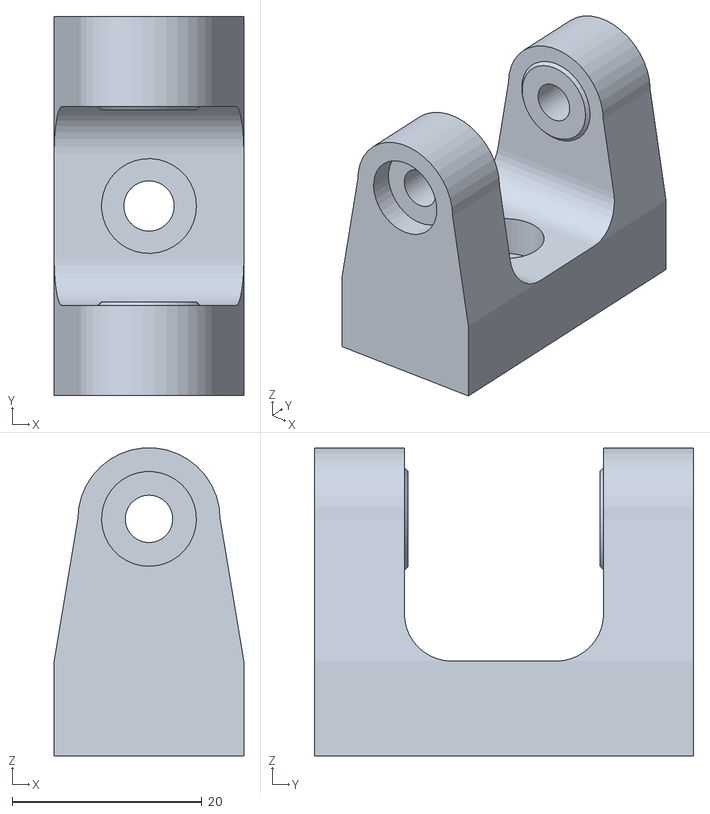
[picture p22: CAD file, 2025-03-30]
CAD/STL Files/Belt Tensioner.STL
20.0 x 40.0 x 32.5

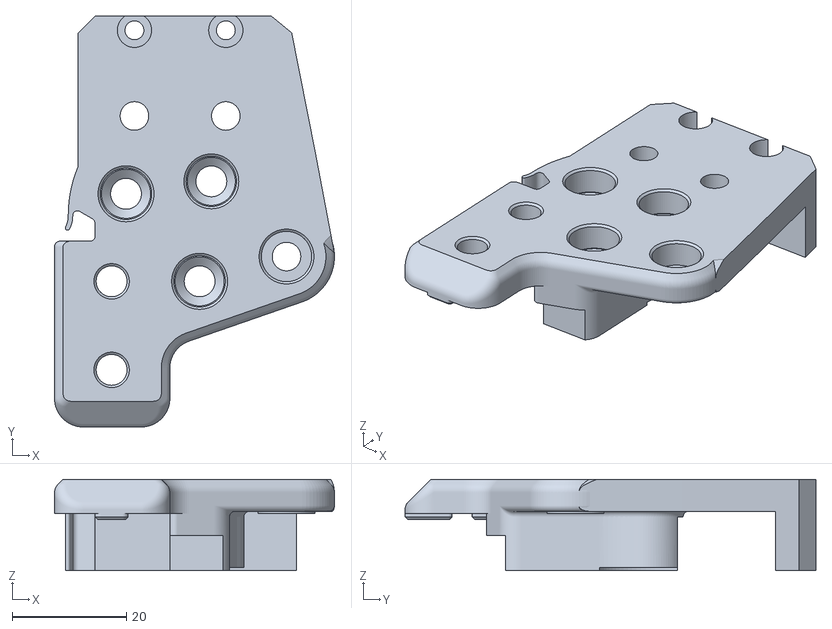
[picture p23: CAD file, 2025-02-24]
CAD/STL Files/Right Y Carriage Top.stl
49.0 x 72.0 x 16.0

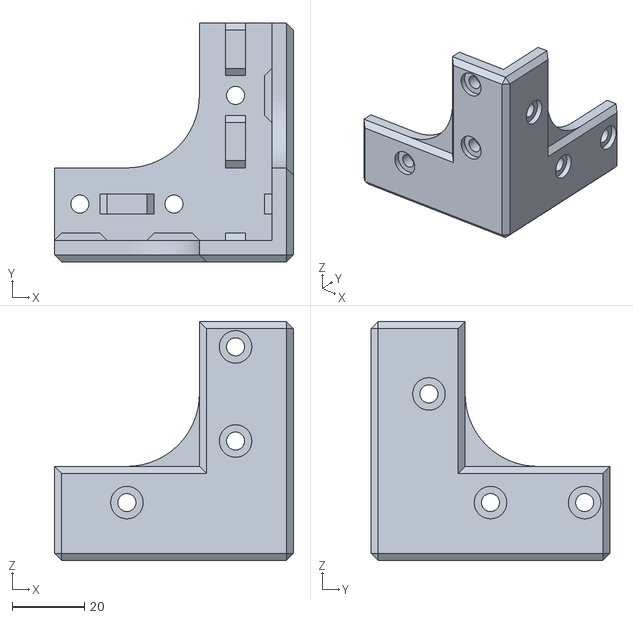
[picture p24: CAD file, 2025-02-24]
CAD/STL Files/Top Corner Bracket.stl
66.0 x 66.0 x 66.0

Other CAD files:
CAD/STL Files/Right Y Carriage Bottom.stl
CAD/STL Files/Z Motor Bracket V3.STL
CAD/STL Files/MGN9 Linear Rail Jig.stl
CAD/STL Files/XY Motor Mount.STL
CAD/STL Files/Ball Screw Bracket V3.STL
CAD/STL Files/Belt Adapter.STL
CAD/STL Files/Idler Mount A.STL
CAD/STL Files/Idler Mount B.stl
CAD/STL Files/Left Y Carriage Bottom.stl
CAD/STL Files/Left Y Carriage Top.stl
CAD/STL Files/MGN12 Linear Rail Jig.stl
CAD/STL Files/X Limit Switch Mount.STL
CAD/STL Files/Z Carriage.stl

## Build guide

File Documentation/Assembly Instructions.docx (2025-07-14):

Andrey Chirikov, Brady Kreil, Gus Hawley,

Harry Zhou, Mikhail Ignatyev, Stephanie Monagan

OPTICAL MODULE

ASSEMBLY INSTRUCTIONS

UBC Manufacturing Engineering

Capstone Project 2024/2025

# 1. Introduction

This document is intended to go over how to assemble the optical module from scratch. The optical module is an automated microscope, designed to be integrated in a self-driving lab. Many components and information will be stored on our GitHub and referenced throughout the document:
https://github.com/ManuCapstone1/OpticalModule/tree/main

# 2. Design Overview

This section provides an overview of the final design. The entire assembly is mounted on 20x20 aluminum extrusions, forming a rigid structural frame. The sample platform is a breadboard, allowing flexible placement of the sample at any position. The platform assembly is supported by two trolleys running along rails, enhancing the rigidity of the structure. It is connected to a ball screw mechanism actuated by a DC motor to ensure precise movement along the Z-axis.

The optical module moves in the XY plane and is mounted on a trolley rail system, similar to the Z-axis setup. However, its movement is controlled by a CoreXY motion system, which uses belts and DC motors for efficient and precise positioning. The CAD model shown in Figure 1 shows the complete design, excluding belts and fasteners. A detailed list of fasteners and their connection points is provided in Appendix A.2.

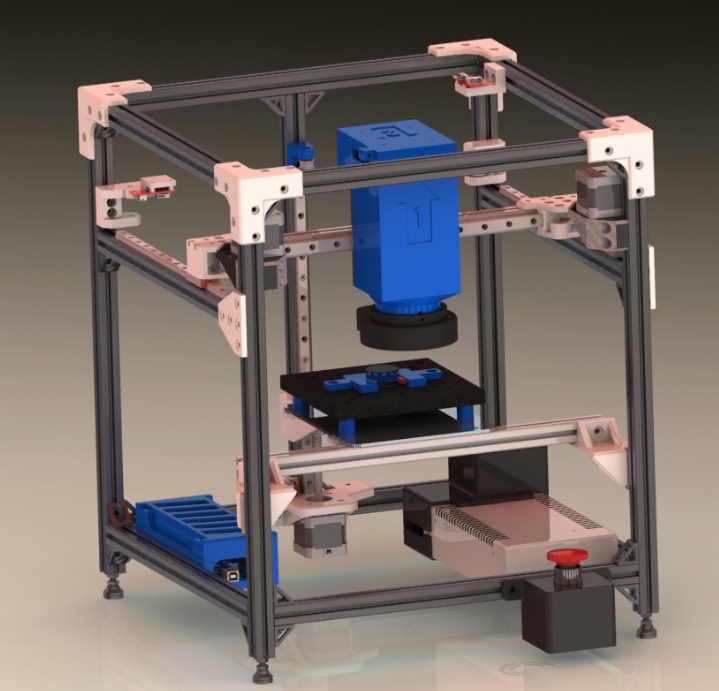
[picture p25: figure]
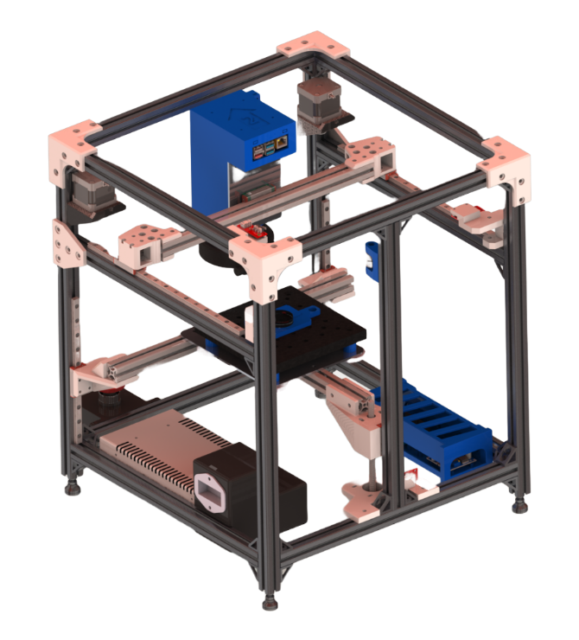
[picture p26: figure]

Figure 1: Front and back view of the main assembly of the project

# 3. BOM

The full list of all the needed parts and tools are found in appendix A.1 – Full Parts List. Parts lists for fasteners and machined parts are also in appendix A. For a more detailed and organized view, an excel spreadsheet is in the GitHub repository in OpticalModule/Documentation/Github_BOM (https://github.com/ManuCapstone1/OpticalModule/blob/main/Documentation/Github%20BOM.xlsx).

# 4. Machined Parts

## 4.1 Frame

The extrusions used for the frame of the module need to be extremely precise and have a flat surface on each end to ensure a square fit between all of the extrusions.

The recommended cutting procedure is as follows:

1. Measure the required extrusion length, adding 5 mm to the specified length. Mark the measurement on the extrusion using a marker. Measure from the factory cut end, when possible, to ensure better cut surface quality.
2. Cut the extrusion using a bandsaw.
3. Set up a milling machine for cutting the extrusions. Secure an adjustable end stop to serve as a reference point for all extrusion pieces. Keep the end stop fixed for pieces of the same length, but adjust it as needed for other lengths.
4. Place the extrusion in a vise, press it against the end stop, and tighten the vise securely.
5. Load an edge finder tool, turn on the spindle, and carefully move the tool against the extrusion’s end-stop edge from the side until it shifts—this marks the zero point, factoring in the edge finder’s radius.
6. Raise the edge finder above the extrusion piece’s edge and verify its position. It should match the radius of the edge finder. If correct, zero the coordinates again—this is the final zero point.
7. Replace the edge finder with a milling tool. For 20x20 extrusions, a 1" tool is recommended. Calculate the final milling position as the desired length plus the tool’s radius.
8. Mill the free end of the extrusion using 0.5 mm passes, finishing with a down milling cut for a better surface finish. Verify the final length, ensuring it falls within the 0.1 mm tolerance.

## 4.2 Plates

The recommended machining procedures for the enclosure backplate, platform baseplate and the Breadboard Platform are described below. For dimensions and other information, reference Appendix A.3 – List of Machined Parts.

Enclosure Backplate

1. Select a metal sheet of the specified thickness. Using a marker, outline the specified length and width according to the drawing.
2. Cut the sheet to size using a shear cutter. For better accuracy, cut slightly beyond the marked dimensions to allow for final adjustments by grinding if needed.
3. Place the sheet on a flat granite surface and use a height gauge to scribe lines indicating the specified hole positions.
4. At each intersection of the scribed lines, use a center punch and hammer to create small dents. This will help guide the drill bit accurately.
5. Prepare M2.5, M3, and M5 drill bits for use with a drill press. Secure the sheet face-up in a vise, ensuring it is tightly clamped.
6. Load the first drill bit into the drill press. Align it with a punched dent and lower it slightly to confirm proper positioning. Adjust the vise if necessary.
  a. Drill through each marked hole, following the specified locations.
  b. Repeat step 6 for each drill bit size.
7. Use a deburring tool to remove any burrs from the back side of the plate.

Base plate

The base plate was fabricated using a waterjet cutter. A correctly sized metal plate was positioned in the machine, and the DXF file containing the final shape was uploaded to the cutter’s computer. The plate was then cut according to standard waterjet cutting procedures.

Breadboard Platform

1. Place the original Breadboard Platform on a flat granite surface. Use a height gauge to scribe lines marking the specified hole positions.
2. At each intersection of the scribed lines, use a center punch and hammer to create small dents to guide the drill bit.
3. Secure the Breadboard Plate firmly in a vise.
4. Select an M6 drill bit suitable for use with a drill press. Load it into the drill press and lower it onto a dent to verify proper alignment. Adjust the vise if necessary.
5. Drill through each marked hole.
6. Use a deburring tool to remove burrs from the opposite side of the plate.

# 5. 3D Printed Parts

## 5.1 Overview

All the .STL files for the parts that need to be printed can be found on the GitHub under OpticalModule/CAD/STL Files/. (https://github.com/ManuCapstone1/OpticalModule/tree/main/CAD/STL%20Files) To see a list of the parts go to the “3D Printed” category in appendix A.1 – Full Parts List. Furthermore, a list of all the fasteners corresponding to each part is in appendix A. – List of Fasteners per Part.

## 5.2 Recommended Settings

Below are the settings and parameters the team used in the slicer to print the 3D printed parts with a FDM printer. The parts were printed with the intention of having good structural integrity and rigidity to prolong the lifespan and reduce vibrations. These settings are suggestions, and users are at liberty to modify them as needed.

One exception to these settings are the jigs for the linear rails. Since they are not used in the final product, nor structurally, standard/weaker settings can be used instead.

Table 1: Recommended printer settings for 3D printed parts.

Parameter | Setting/Parameter | Notes
Material | ABS, PLA, PLA +, PETG | Stronger materials will work as well but are not needed.
Resolution | 0.02 mm
Infill | ~50%
Infill Pattern | Cubic | Good for strength in all directions.
Supports | >45 degrees
Shell Thickness | 1.2 mm in both directions.

## 5.3 Camera Carriage

The STL file “EnclosureBase” is the main body of the camera carriage. Orient the part as shown below in gure 2, as it ensures a nice outer finish and minimal shifting errors and cracking. When the print is complete, removing the supports is difficult. If needed, use pliers, a Dremel and/or similar tools.

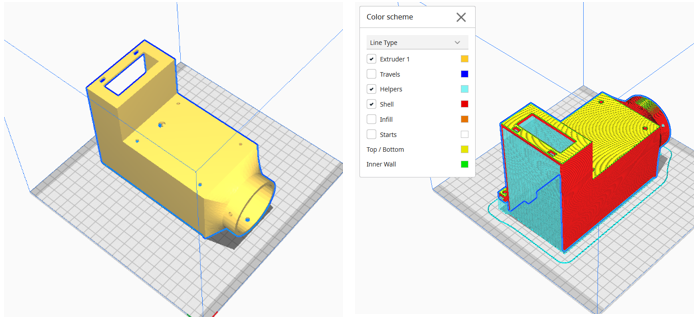
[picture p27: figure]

Figure : Orientation of how the "EnclosureBase" STL file should be placed on the slicer.

## 5.4 Mirrored Brackets

Two STL files “XY Motor Mount” and “Z Carriage” need two parts each, one as is, and the other mirrored. Use the slicer to mirror one of the parts. Figure and Figure 4 show how the parts should be mirrored. Note that the parts in the figures were placed to show how the parts should be mirrored, not how the parts should be oriented for printing.

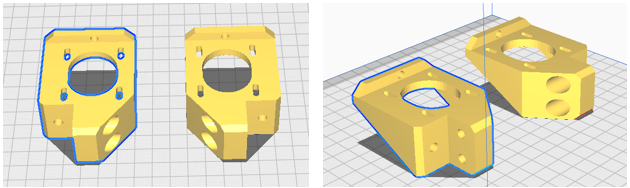
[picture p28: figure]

Figure 3: View of how "XY Motor Mount" STL files should be mirrored in the slicer.

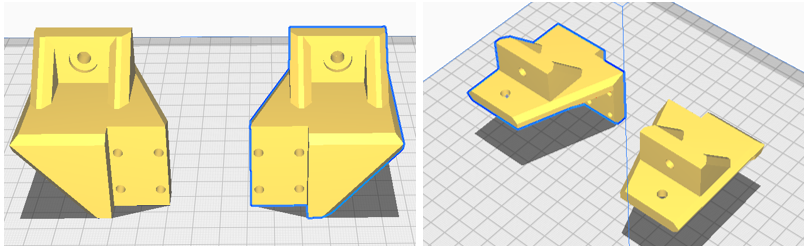
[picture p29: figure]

Figure : View of how "Z Carriage" STL File should be mirrored in the slicer.

# 6. Assembly

## 6.1 Frame Assembly

1. To assemble the frame, start by constructing the sides. Lay two 465 mm extrusions on a flat surface and position three 370 mm extrusions perpendicularly between them.
2. Secure the 370 mm pieces to one of the 465 mm extrusions using M5x10 fasteners and M5 T-nuts (detailed list of fasteners in Appendix A.2), then repeat for the other 465 mm extrusion.
3. Check squareness by standing the subassembly vertically and using a bubble gauge to verify perpendicularity. Adjust the brackets as needed to center the bubble.
4. Next, lay assembled side flat and attach four 370 mm extrusions vertically using M5x10 fasteners and M5 T-nuts, ensuring proper alignment.
5. Attach four brackets—two on each side—to the 395 mm extrusion, then slide it into place parallel to the 465 mm extrusions.
6. Secure the second assembled side to complete the frame, then verify squareness again with a bubble gauge, adjusting as necessary.
7. Then, install the 3D-printed top corner brackets and T-brackets using M5x10 fasteners and M5 T-nuts.
8. Add X limit switch mount by attaching limit switch to the mount using M3x16 fasteners and M3 nuts and attaching the mount to the extrusion using M5x10 fasteners and M5 T-nuts.
9. Finally, install linear rails by using M3x8 fasteners and M3 T-nuts and following the linear rail alignment procedure outlined in a section below.

## 6.2 Camera Carriage

1. To assemble the Camera Carriage, start with the Enclosure Backplate by attaching the metal plate to the 3D-printed Enclosure Base using four M3x4 fasteners and M3 Hex Nuts.
2. Before proceeding further, complete the Belt Assembly system (see below). Next, screw the threaded Camera into the Lens and mount them to the Enclosure Base using a 1/4-20 fastener, placing two 1/4" Washers between the camera and the enclosure.
3. Secure the Lens by positioning the Ring Light at the bottom of the Enclosure Base and fastening it with the included M4 Thumb screws, which will later allow for perpendicularity adjustments.
4. Mount the Raspberry Pi to the bottom of the Upper Enclosure Cover using four M2.5x16 fasteners and M2.5 Hex Nuts, ensuring its external ports face outward.
5. Finally, attach the Upper Enclosure Cover to the Enclosure Base and secure them with the Front Enclosure Cover. Refer to Figure 5 for an exploded view of these steps and Appendix A.2 for a detailed list of fasteners.

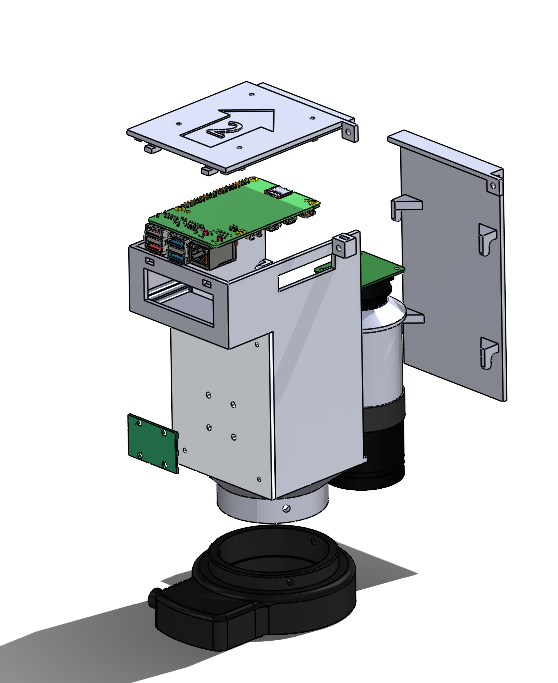
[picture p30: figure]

Figure 5: Camera carriage assembly; exploded view

## 6.3 Belt Assembly

The motion in the X-Y plane is controlled using a CoreXY belt configuration. In this motion strategy, the two motors work together to move the carriage in both the X and Y directions. Consequently, the left and right motors are designated as Motor A and Motor B, respectively. Each motor is associated with its own belt, which runs from one side of the carriage assembly, through a set of idlers, around the motor, and back to the other side of the carriage. In this CoreXY application, the A and B loops are stacked vertically in the Z direction, with the B loop always above the A loop. The ends of both loops are clamped between the aluminum backplate of the carriage enclosure and the belt adapter, which has four sets of teeth to mesh with the four belt ends. More information about the CoreXY theory and governing equation can be found at corexy.com.

The assembly of the X-Y belt system is as follows (refer to Appendix A.2 for the detailed fastener list):

1. Begin by assembling the Y carriage, which includes the X-axis gantry aluminum extrusion and the left and right brackets.
  a. Attach the linear rail and trolley to the front face of the aluminum extrusion using M3x8 fasteners and T-nuts.
  b. Use M5x40 fasteners and hex nuts to attach the upper and lower halves of the brackets around the extrusion.
  c. Install the idlers, with the front idler consisting of two smooth bearings and the back idler a toothed idler. They are installed using M5x40 fasteners with a washer above and below.
  d. Attach the Y carriage to the two Y trolleys using four M3x12&x30 fasteners.
2. Assemble the XY motor mounts with the stepper motors using M3x8 fasteners and attach the pulleys to the stepper motors.
3. Install the motor mounts on the front two vertical extrusions using M5x10 fasteners. Pay attention to the height of the pulleys. Pulley B should be aligned with the upper set of idlers, while Pulley A should be aligned with the lower set of idlers. This can be done roughly at first and then adjusted.
4. Assemble idler mounts A and B. Each idler mount contains two toothed idlers and three washers on an M5x40 fastener. The limit switch is installed using M3x16 fasteners.
5. Install the idler mounts on the rear left and right vertical extrusions. Idler mount A includes a mounting point for the Y limit switch and should be installed on the left side (closest to Motor A).
6. Assemble, but do not install, the belt tensioner. The belt tensioner includes four smooth bearings forming two smooth idlers. An M5x45 fastener runs through the bearings, and a hex nut is used between the bearings to align them.
7. Install belt loop A. Belt A runs from the lower left slot on the belt adapter, with the teeth facing the trolley, around the smooth idler on the left Y carriage, around Pulley A, around the lower idler on idler mount A, around the lower idler on idler mount B, around the toothed pulley on the right Y carriage, and to the lower right slot on the belt adapter.
8. Install belt loop B. Belt loop B follows the opposite path using the upper set of idlers and belt adapter slots.
9. Clamp the belts by installing the carriage enclosure. Start by temporarily taping the belt clamp to the X-axis trolley. Then, while holding all four belt ends in position on the belt adapter, use four M3x8 fasteners to attach the carriage enclosure to the trolley and belt adapter, clamping everything together.
10. Install the belt tensioner on the back center vertical extrusion using an M5x10 fastener and place the belts in position.

## 6.4 Platform Assembly

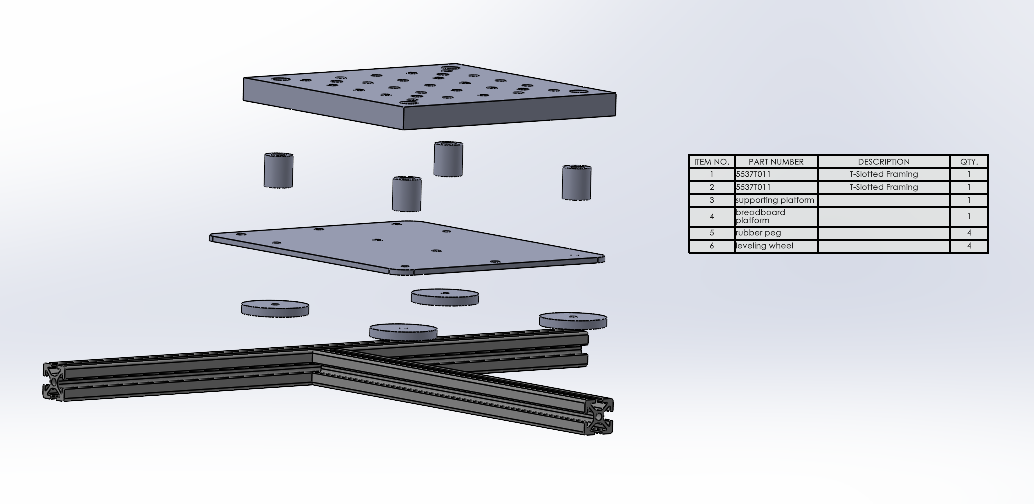
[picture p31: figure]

Figure 6: Exploded view of the platform and relevant bill of materials

1. First, secure the three Z-axis linear rails to the frame using five M3x8 fasteners and M3 T-Nuts (see Linear Rail Alignment).
2. Attach the Z Carriage Brackets to the trolleys on the two front linear rails with four M3x12 fasteners each.
3. Next, mount a 370mm aluminum extrusion to the Z Carriage Brackets using two M5x10 fasteners and M5 T-Nuts per side.
4. Attach the Z Motor Bracket under the rear linear rail with four M5x10 fasteners and M5 T-Nuts.
5. Secure the Z-axis stepper motor beneath the bracket with four M3x12 fasteners, then mount the limit switch using two M3x12 fasteners and M3 Hex Nuts.
6. Attach the Ball Screw Bracket to the trolley on the rear linear rail with four M3x12 fasteners. Secure the 255mm aluminum extrusion to the Ball Screw Bracket with six M5x10 fasteners and M5 T-Nuts.
7. Fasten the Ball Screw Bracket to the Ball Screw using two M4x14 fasteners with M4 Hex Nuts.
8. Join the two aluminum extrusions with corner brackets using four M5x10 fasteners, each with an M5 T-Nut and M5 Washer.
9. Attach the Supporting Platform to the extrusions using six M5x10 fasteners, M5 T-Nuts, and M5 Washers.
10. Finally, secure the Breadboard Platform to the Supporting Platform with the M4 fasteners included with the spacers and knobs. (See Appendix A.2 for detailed fastener list)

## 6.5 Linear Rail Alignment

To install the linear rails, lay the rail onto the extrusion, and use the 3D printed jigs, one on each end, to align the rail properly. The Y and Z rails use the “MGN9H Linear Rail Jig” and the X rail uses the “MGN12H Linear Rail Jig”. See the GitHub repository under OpticalModule/CAD/STL Files (https://github.com/ManuCapstone1/OpticalModule/tree/main/CAD/STL%20Files) for the STL files and the source link with pictures.

## 6.6 Z Motor and Ball Screw Alignment

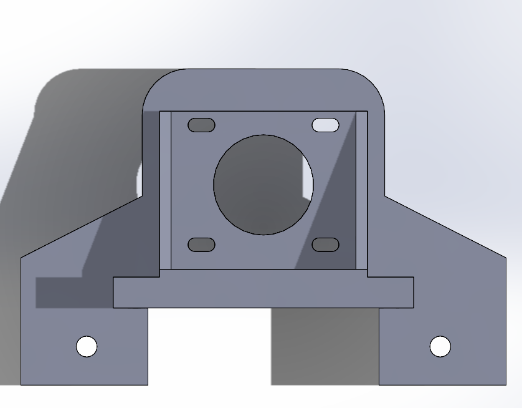
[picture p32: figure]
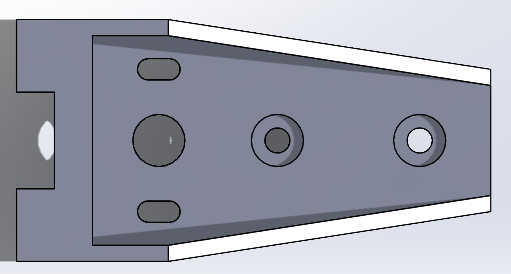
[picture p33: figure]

Figure 7: z-axis assembly top view Figure: 8 lead screw bracket top view

1. First install z-axis assembly onto the aluminum extrusions with 4 M5x10 fasteners and M5 T-nuts.
2. Attach one Nema 17 stepper motors with 4 M3x8 fasteners.
3. Connect the lead screw and the stepper motor via a coupler.
4. Connect the z axis limit switch and secure them with 2 M3x8 fasteners and 2 M3 hex nuts.
5. Attach lead screw bracket to linear rail via 4 M3x8 fasteners.
6. Attach lead screw flange to lead screw bracket via M3x12 fasteners with M3 hex nuts.
7. Adjust the XY position of lead screw with z-axis assembly and lead screw bracket flexible slots until lead screw is perpendicular to stepper motor. Turn the leadscrew until there is little resistance moving from bottom to top.

## 6.7 Electrical Assembly

### 6.8 Overview

The below diagram is a representation of the electrical components involved in this project. Since the power supply is rated at 24V and 14.6 A (Max), the voltage needs to be converted to 3 levels to accommodate CNC shield (24V), ring light (12V) and Raspberry pi (5V) respectively. Furthermore, stepper motors and limit switches (NO) are connected to CNC shield via their designated pins. An emergency stop is designed to terminate and reset the program for CNC shield. Arduino Uno is powered by the Raspberry Pi via a serial connection (USB-A to USB-B). Detail lists of Assembled List and BOM List can be found in Appendix A.6 and A.7.

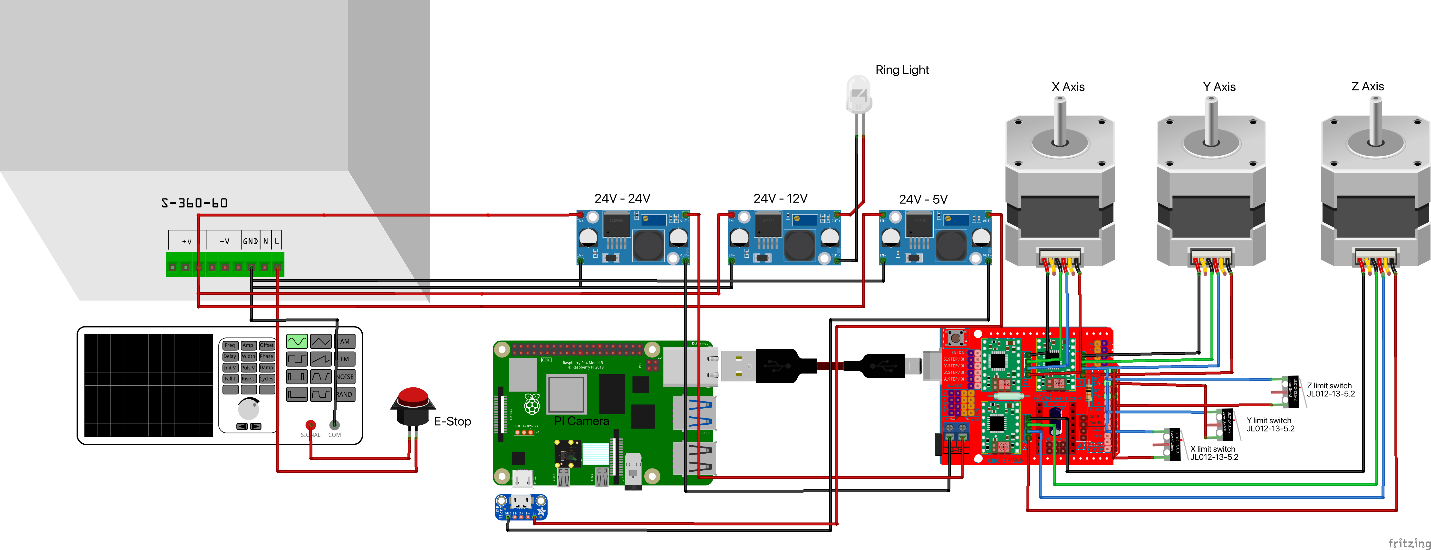
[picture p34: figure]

Figure 9: Electrical components their connections

### 6.9 E-STOP

The E-Stop is installed upstream of the DC power supply on the live wire between the fused C14 connector and the 120V input terminal of the DC power supply. Ensure ferrules are added to the wires before they are installed in the screw terminals of the E-Stop. After all electrical components are installed, the system should be ground checked before it is powered on to ensure safe operation.

### 6.10 Buck Converters

The three buck converters power the ring light, the Raspberry Pi, and the CNC shield. The input side of the buck converters should be wired in parallel to the 24V supplied by the DC power supply. For the ring light, the buck converter output should be tuned to 12V using a multimeter and then connected to a DC barrel plug. For the Raspberry Pi, the buck converter should be tuned to 5.1V and then connected to a USB-C breakout board. For the CNC shield, the buck converter should be tuned to between 15 and 24V and connected directly to the power input terminals of the CNC shield.

# 7. Software Setup

## 7.1 Raspberry Pi Settings

Setting Up Raspberry Pi Using Raspberry Pi Imager

Setting up the Raspberry Pi began with using the Raspberry Pi Imager tool. First, download and install Raspberry Pi Imager from the official Raspberry Pi website (https://www.raspberrypi.com/software/). Insert a microSD card or USB drive into your computer and launch the Imager. Click on "Choose OS" and select the preferred Raspberry Pi OS version. For this project, we used the default Raspberry Pi OS (64-bit). Next, click on "Choose Storage" and select the microSD card or USB drive. Next, click on the settings icon to enable SSH, set up a username and password, and configure Wi-Fi if needed. The username and password selected for this project was ‘microscope’. Once configured, click "Write" to flash the OS onto the microSD card or USB drive. After completion, eject the storage device and insert it into the Raspberry Pi. Power on the Raspberry Pi, and it will boot into the installed OS.

## 7.2 Networking

Setting Up Static IP Addresses;

A static IP address was configured on both the Raspberry Pi and Mini PC to establish a direct Ethernet connection between the devices. The Raspberry Pi is physically connected to the mini PC via an Ethernet cable from the Raspberry Pi’s Ethernet port to the PC’s Ethernet port.

The first step was to configure the computer’s static IP address. On Windows, navigate to the Control Panel and open the Network and Sharing Center. Click on Change adapter settings, right-click the Ethernet adapter, and select Properties. Choose Internet Protocol Version 4 (TCP/IPv4), then select ‘Use the following IP address’. Enter an IP address and set the subnet mask to 255.255.255.0. On the Mini PC used for the project, the static IP was configured to be “192.168.1.10”. Leave the default gateway blank. Click OK to save the changes.

To configure the Raspberry Pi’s static IP address, open a terminal, and type ‘ip r | grep default’ and save the gateway. Next, type ‘nmtui’ and select Edit a Connection, followed by Wired Connection. Under IPv4 Configuration, press add and enter the IP address you wish to use. For this project, we used “192.168.1.111” as our address. Also, enter the previously found gateway under Gateway. Afterward, navigate to OK at the bottom of the screen, followed by Back and Quit. Now, type ‘sudo systemctl restart NetworkManager’ into the terminal. To check if the Static IP address is working, type ‘hostname -I’ into the terminal.

Once both devices are set up, you can test the connection by opening a terminal or Command Prompt on the computer and running `ping 192.168.1.111`. A successful connection will return response packets from the Raspberry Pi.

Remote Connection via VNC Viewer:

To remotely access the Raspberry Pi’s desktop environment, VNC Viewer was used for this project. To enable the functionality on the Raspberry Pi, first, enable VNC by opening a terminal and running ‘sudo raspi-config’. Navigate to Interface Options, select VNC, and enable it. Then, install the RealVNC server if it is not already available using ‘sudo apt update’ and ‘sudo apt install realvnc-vnc-server’ in the terminal.

On the PC, download and install VNC Viewer from the official RealVNC website (https://www.realvnc.com/en/connect/download/viewer/). To remotely access the Raspberry Pi, open VNC Viewer and enter the VNC server ‘bestcapstone’ with the password ‘microscope’ if the devices are connected to the same wifi network. Otherwise, enter the Raspberry Pi’s static IP address (192.168.1.111) in the address bar with the password ‘microscope’. If prompted, enter the Raspberry Pi’s username, which is also ‘microscope’. Once connected, the Raspberry Pi’s desktop interface will be accessible remotely, allowing full control over the device without needing a monitor, keyboard, or mouse.

## 7.3 Windows PC

### 7.3.1 Ethernet

For whichever PC, ensure that it has an ethernet port, or purchase a dongle, so that it can connect to the Raspberry Pi.

### 7.3.2 Folder Directories

Setup and create folders in an organization like so, and modify gui.py (see GitHub (https://github.com/ManuCapstone1/OpticalModule/blob/main/Programming%20Files/pc_files/gui.py)) so that it matches the folder paths you created. This structure is not essential to the program, however, ensure that you are mindful of the folder locations when making modifications to gui.py.

- images
  - GUI
  - complete
    - stitching
    - sampling
  - buffer
    - stitching
    - sampling
    - camera_tests

### 7.3.3 Fiji (ImageJ)

Download Fiji at:

https://imagej.net/software/fiji/downloads

Setting up the Image Stitching Macro in Fiji (ImageJ)

1. Record Macro

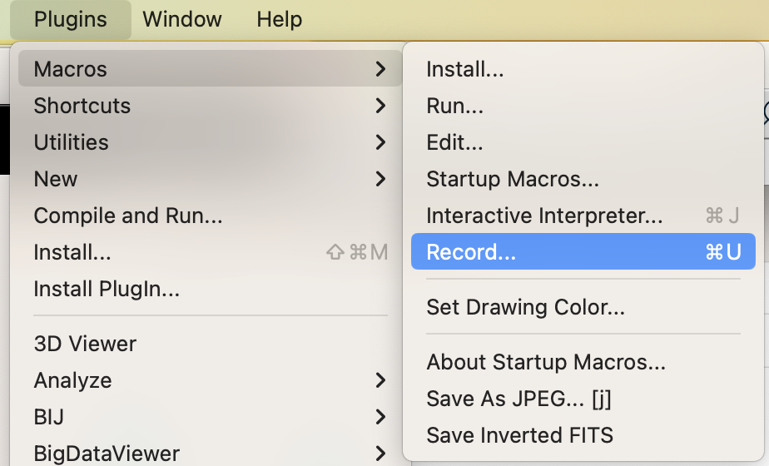
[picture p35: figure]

2. Image Stitching Plug in

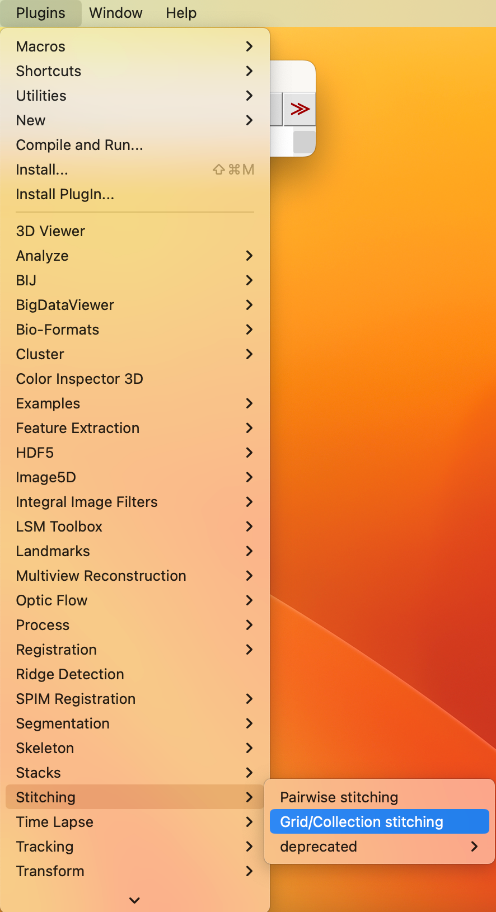
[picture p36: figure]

3. Configure Settings (note the Type and Order of scanning do not change)

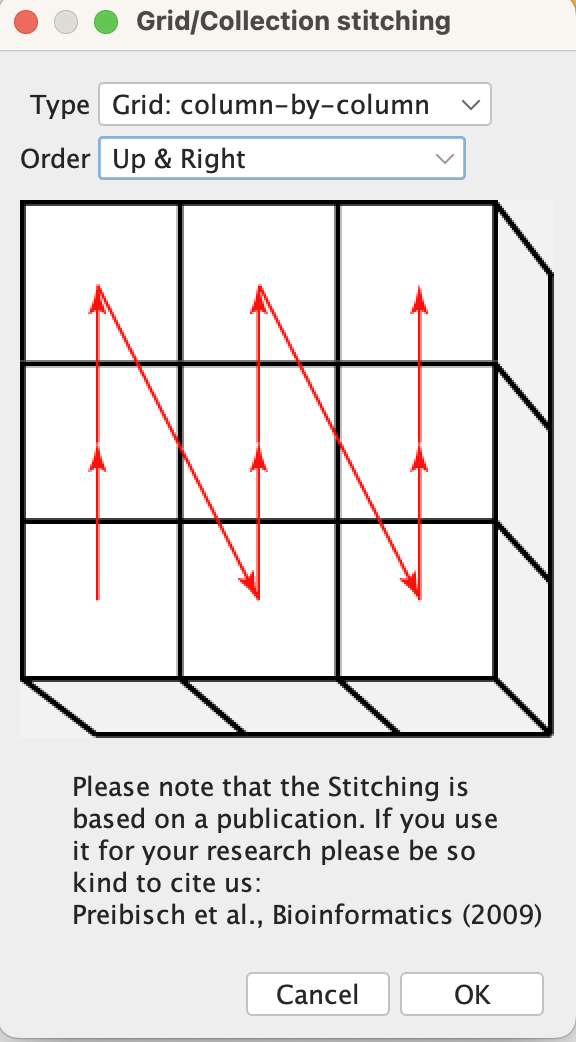
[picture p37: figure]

4. Run the plug-in and save the macro (.ijm file)

The macro written for this project is also available for use at this link:

https://github.com/ManuCapstone1/OpticalModule/tree/main/Programming%20Files/fiji

# Appendix

## A.1 – Full Parts List

Table 2: List of all parts and tools needed to build the optical module.

Category | Part | Additional Specs or Notes | Website for Specific Parts | Needed Quantity/Size
Electrical | Arduino Uno | | | 1
Electrical | Arduino CNC Shield V3.00 | Includes 3 drivers, E-Stop pins | | 1
Electrical | Mech Endstop V1.2 with Cable | | | 3
Electrical | E-Stop | Twist release, terminal blocks, NC. 24VDC and 10A. | | 1
Electrical | DC Power Supply | 24VDC, ~15A, 50/60Hz | | 1
Electrical | Power Inlet | 250V, 15A | | 1
Electrical | Raspberry Pi | Pi 5, RAM 2GB | | 1
Electrical | SD Card for Raspberry Pi | Class 10, 32GB or more | | 1
Electrical | Stepper Motor | NEMA 17, 1.8deg, 1A | | 3
Electrical | Stepper Motor Cables | 4 Pin, < 60cm long | | 3
Electrical | Ethernet Cable | 90 degree corner facing upwards, cable in direction of locking tab. | | 1
Electrical | USB C to USB C Cable | >40cm long | | 1
Electrical | USB C Female Breakout Board PCB | For powering Raspberry Pi from power supply. | | 1
Electrical | USB-A to USB-B Cable | > 50cm long | | 1
Electrical | USB A 90 deg corner adapter | For plugging in USB A - USB B cable into raspberry Pi | | 1
Electrical | microHDMI cable | For displaying Raspberry Pi if needed | | 1
Electrical | DC-DC Step Down Buck Converter Module | LM2596 | | 3
Electrical | 12 AWG Silicone Copper Wires | For wiring power supply to rocker. | | >100 cm
Electrical | 22 AWG Solid-Core Insulated Wires | For wiring Step Down Converters | | > 40 cm
Electrical | Ring Terminal Connectors | | | 10
Electrical | Spade Terminal Connectors | | | 6
Electrical | Cable Mesh Sleeve | >1 m, > 3/8" | | 1
Electrical | Cable Ties | | | ~5
Electrical | PC | Ethernet Port. Interfaces with Raspberry Pi, storage for images. Runs Windows | | 1
Electrical | USB Wifi Dongle | Only if needed. To get PC Wifi. | | 1
Mechanical | Ball Screw and Nut | 150 mm long, M8, 2mm per turn | Link (https://www.mcmaster.com/6624k67/) | 1
Mechanical | Lubricant | PTFE Dry lubricant or Superlube | | 1
Mechanical | Timing Belt | GT2, 6mm | | >2 m
Mechanical | Belt Pulley Toothed | GT2, 5mm bore, 6mm, toothed | | 2
Mechanical | Pulley Idler Toothed | GT2, 5mm bore, 6mm, toothed idler | | 6
Mechanical | Bearings | F695-2RS, 5x13x4mm, flanged | | 8
Mechanical | Coupler (motor to balls screw) | 5mm to 8mm | | 1
Mechanical | PLA, PLA +, ABS | Spool (1kg) | | 2
Mechanical | Linear rails X | MGN12H 300mm | | 1
Mechanical | Linear rails Y | MGN9H 350mm | | 2
Mechanical | Linear Rails Z | MGN9H 200mm | | 3
Mechanical | Spacers and Knobs for Stage | Package of 4 spacers, M4 fastener, and knobs. Typically used for 3D printers | | 1
Mechanical | Bubble gage | | | 1
Mechanical | Leveling Feet | Adjustable height, max M6 screws, dampening | Link (https://www.mcmaster.com/5537T982/) | 4
Machined | Breadboard Stage | 150x150x13mm | Link (https://www.aliexpress.com/item/1005006895797933.html?curPageLogUid=qSWfg5B0oj7o&utparam-url=scene%3Asearch%7Cquery_from%3A) | 1
Machined | Mounting plate for stage | 150x185mm, thickness 4-5mm. See engineering drawing. | | 1
Machined | Metal plate (camera carriage) | 105x80x5mm. See engineering drawing | | 1
Machined | 2020 V-Slot Aluminum Extrusion | 370mm x 11 465mm x4 395mm x1 330mm x1 255mm x1 | | 1
Optical | Camera | Raspberry Pi HQ Camera CS 12.3 MP | Link (https://www.pishop.ca/product/raspberry-pi-hq-camera-cs/) | 1
Optical | Lens | 100X Industrial Microscope Lens, C/CS-Mount, 0.12X ~ 1.8X | Link (https://www.pishop.ca/product/100x-industrial-microscope-lens-c-cs-mount-compatible-with-raspberry-pi-hq-camera-cs/) | 1
Optical | Ring Light | 62.5mm inside, 92.5mm outside diameter. | Link (https://www.amazon.ca/Vision-Scientific-VMLIFR-09B-Adjustable-Illuminator/dp/B07VR2LJJL) | 1
Fastener | 1/4" Washer | | | 2
Fastener | 1/4-20 x 1/2" BHCP or SHCP | | | 1
Fastener | 2020 Corner Bracket | | | 34
Fastener | M2.5 Hex Nut | | | 20
Fastener | M2.5x14 BHCP or SHCP | | | 16
Fastener | M2.5x16 FHCP | | | 4
Fastener | M3 Drop T-nut | | | 34
Fastener | M3 Hex Nut | | | 10
Fastener | M3x4 BHCP or SHCP | | | 4
Fastener | M3x8 BHCP or SHCP | | | 16
Fastener | M3x8 SHCP | | | 34
Fastener | M3x12 BHCP or SHCP | | | 18
Fastener | M3x16 BHCP or SHCP | | | 4
Fastener | M3x30 BHCP or SHCP | | | 4
Fastener | M4 Hex Nut | | | 2
Fastener | M4x8 BHCP or SHCP | | | 2
Fastener | M4x14 BHCP or SHCP | | | 2
Fastener | M4x20 BHCP or SHCP | | | 2
Fastener | M5 Drop T-Nut | | | 168
Fastener | M5 Hex Nut | | | 12
Fastener | M5 Washers | | | 74
Fastener | M5x10 BHCP | | | 168
Fastener | M5x40 BHCP or SHCP | | | 2
Fastener | M5x40 SHCP | | | 8
Fastener | M5x45 BHCP or SHCP | | | 1
Fastener | M6x14 BHCP or SHCP | | | 2
3D Printed | Enclosure Base V2 | | | 1
3D Printed | Enclosure Cover Front | | | 1
3D Printed | Enclosure Cover Upper | | | 1
3D Printed | Belt Adapter | | | 1
3D Printed | Idler Mount B | No limit switch mount. | | 1
3D Printed | Idler Mount A | Includes limit switch mount. | | 1
3D Printed | XY Motor Mount | One as is, the other mirrored | | 2
3D Printed | Z Carriage | One as is, the other mirrored | | 2
3D Printed | Ball Screw Bracket | | | 1
3D Printed | Z Motor Bracket | | | 1
3D Printed | Housing Base | | | 1
3D Printed | Housing Top | | | 1
3D Printed | Belt Tensioner | | | 1
3D Printed | estop enclosure bottom | | | 1
3D Printed | estop enclosure top | | | 1
3D Printed | Power Supply Housing | | | 1
3D Printed | Sample Holder Pin | Add a spring from a pen to the cylindrical part of the pin. | | 1
3D Printed | Sample holder clamping plate | | | 1
3D Printed | Sample holder base | | | 1
3D Printed | Left Y Carriage Top | | GitHub rolohuan (https://github.com/rolohaun/SimpleCore/tree/main/CAD) | 1
3D Printed | Left Y Carriage Bottom | | GitHub rolohuan (https://github.com/rolohaun/SimpleCore/tree/main/CAD) | 1
3D Printed | Right Y Carriage Top | | GitHub rolohuan (https://github.com/rolohaun/SimpleCore/tree/main/CAD) | 1
3D Printed | Right Y Carriage Bottom | | GitHub rolohuan (https://github.com/rolohaun/SimpleCore/tree/main/CAD) | 1
3D Printed | X Limit Switch Mount | | | 1
3D Printed | MGN9 Linear Rail Jig | Print at standard/weaker settings. | Thingiverse (https://www.thingiverse.com/thing:5903898/files) | 2
3D Printed | MGN12 Linear Rail Jig | Print at standard/weaker settings. | Thingiverse (https://www.thingiverse.com/thing:5903898/files) | 2
3D Printed | T-bracket | | Thingiverse (https://www.thingiverse.com/thing:2503622/files) | 4
3D Printed | Top Corner Bracket | | Thingiverse (https://www.thingiverse.com/thing:2655498) | 4
3D Printed | Ball Screw Knob | Scaled at 97% | Thingiverse (https://www.thingiverse.com/thing:3014508/files) | 1
3D Printed | Cable Management Clips | | Thingiverse (https://www.thingiverse.com/thing:4612080/files) | ~20
Tools | Metric Allen Keys | | | 1
Tools | Wire Cutter | | | 1
Tools | Crimping Tool | | | 1
Tools | Soldering Iron | | | 1
Machining Tools | Band Saw | If needed, for cutting extrusions.
Machining Tools | Milling Machine | If needed, for cutting extrusions.
Machining Tools | Power Drill | If needed, for tapping holes for extrusion leveling feet.
Machining Tools | Tap and Drill for M6 Holes | If needed, for cutting mounting plate.
Machining Tools | Waterjet Cutter

## A.2 – List of Fasteners per Part

Table 3 - List of fasteners corresponding to each part.

Row Labels | Sum of # Parts | Sum of Total
Ball Screw Bracket | 5 | 20
M3x8 BHCP or SHCP | 1 | 4
M4 Hex Nut | 1 | 2
M4x14 BHCP or SHCP | 1 | 2
M5 Drop T-Nut | 1 | 6
M5x10 BHCP | 1 | 6
Belt Tensioner | 4 | 5
M5 Drop T-Nut | 1 | 1
M5 Hex Nut | 1 | 2
M5x10 BHCP | 1 | 1
M5x45 BHCP or SHCP | 1 | 1
Enclosure Base | 5 | 15
1/4" Washer | 1 | 2
1/4-20 x 1/2" BHCP or SHCP | 1 | 1
M3 Hex Nut | 1 | 4
M3x4 BHCP or SHCP | 1 | 4
M3x8 BHCP or SHCP | 1 | 4
Enclosure Cover Upper | 2 | 8
M2.5 Hex Nut | 1 | 4
M2.5x16 FHCP | 1 | 4
E-Stop Housing | 2 | 4
M5 Drop T-Nut | 1 | 2
M5x10 BHCP | 1 | 2
Frame | 4 | 238
2020 Corner Bracket | 1 | 34
M5 Drop T-Nut | 1 | 68
M5 Washers | 1 | 68
M5x10 BHCP | 1 | 68
Housing Base | 2 | 32
M2.5 Hex Nut | 1 | 16
M2.5x14 BHCP or SHCP | 1 | 16
Housing Top | 2 | 6
M5 Drop T-Nut | 1 | 3
M5x10 BHCP | 1 | 3
Idler Mount A | 6 | 10
M3 Hex Nut | 1 | 2
M3x16 BHCP or SHCP | 1 | 2
M5 Drop T-Nut | 1 | 2
M5 Hex Nut | 1 | 1
M5x10 BHCP | 1 | 2
M5x40 BHCP or SHCP | 1 | 1
Idler Mount B | 4 | 6
M5 Drop T-Nut | 1 | 2
M5 Hex Nut | 1 | 1
M5x10 BHCP | 1 | 2
M5x40 BHCP or SHCP | 1 | 1
Left Y Carriage | 6 | 18
M3x12 BHCP or SHCP | 1 | 2
M3x30 BHCP or SHCP | 1 | 2
M5 Drop T-Nut | 1 | 3
M5 Hex Nut | 1 | 4
M5x10 BHCP | 1 | 3
M5x40 SHCP | 1 | 4
Linear Rail X | 2 | 10
M3 Drop T-nut | 1 | 5
M3x8 SHCP | 1 | 5
Linear Rail Y | 4 | 28
M3 Drop T-nut | 2 | 14
M3x8 SHCP | 2 | 14
Linear Rail Z | 6 | 30
M3 Drop T-nut | 3 | 15
M3x8 SHCP | 3 | 15
Mounting plate for stage | 3 | 18
M5 Drop T-Nut | 1 | 6
M5 Washers | 1 | 6
M5x10 BHCP | 1 | 6
Power Supply Housing | 2 | 4
M4x8 BHCP or SHCP | 1 | 2
M4x20 BHCP or SHCP | 1 | 2
Right Y Carriage | 6 | 18
M3x12 BHCP or SHCP | 1 | 2
M3x30 BHCP or SHCP | 1 | 2
M5 Drop T-Nut | 1 | 3
M5 Hex Nut | 1 | 4
M5x10 BHCP | 1 | 3
M5x40 SHCP | 1 | 4
Sample Holder | 1 | 2
M6x14 BHCP or SHCP | 1 | 2
T-Bracket | 8 | 40
M5 Drop T-Nut | 4 | 20
M5x10 BHCP | 4 | 20
Top Corner Bracket | 8 | 72
M5 Drop T-Nut | 4 | 36
M5x10 BHCP | 4 | 36
X Limit Switch Mount | 4 | 8
M3 Hex Nut | 1 | 2
M3x16 BHCP or SHCP | 1 | 2
M5 Drop T-Nut | 1 | 2
M5x10 BHCP | 1 | 2
XY Motor Mount | 6 | 20
M3x8 BHCP or SHCP | 2 | 8
M5 Drop T-Nut | 2 | 6
M5x10 BHCP | 2 | 6
Z Carriage | 6 | 16
M3x12 BHCP or SHCP | 2 | 8
M5 Drop T-Nut | 2 | 4
M5x10 BHCP | 2 | 4
Z Motor Bracket | 4 | 16
M3 Hex Nut | 1 | 2
M3x12 BHCP or SHCP | 1 | 6
M5 Drop T-Nut | 1 | 4
M5x10 BHCP | 1 | 4
Total | NA | 644

## A.3 – List of Machined Parts

Table 4: List of parts that need to be machined and links to their instructions.

Part | Engineering Drawing | Link to Instructions
Supporting Platform | CAD/Engineering Drawings/supporting platform.pdf (https://github.com/ManuCapstone1/OpticalModule/blob/main/CAD/Engineering%20Drawings/supporting%20platform.pdf) | Plates
Breadboard Platform | CAD/Engineering Drawings/breadboard platform.pdf (https://ubcca.sharepoint.com/teams/ubcst-gr-MANU430SelfDrivingMaterialsCharacterization/Shared%20Documents/General/Deliverables/CAD/Engineering%20Drawings/bre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) | Plates
2020 V-Slot Aluminum Extrusions (Frame) | CAD/Engineering Drawings/430 Main project assy.pdf (https://github.com/ManuCapstone1/OpticalModule/blob/main/CAD/Engineering%20Drawings/430%20Main%20project%20assy.pdf) | Frame
Enclosure Backplate | CAD/Engineering Drawings/Enclosure Backplate.pdf (https://github.com/ManuCapstone1/OpticalModule/blob/main/CAD/Engineering%20Drawings/Enclosure%20Backplate.pdf) | Plates

## A.4 – Assembly List - Electronics

Table 5: List of parts that need to be assembled for electronics

Label | Part Type | Properties
24V - 12V | LM2596 step down module | type LM2596 step down
24V - 24V | LM2596 step down module | type LM2596 step down
24V - 5V | LM2596 step down module | type LM2596 step down
A1 | Raspberry Pi 5 | processor Broadcom 2711, Quad-core Cortex-A76 64-bit SoC @ 2.4GHz; variant Raspberry Pi 5
Arduino CNC Shield V3.00 1 | Arduino_CNC_V3.00 | variant variant 2
Part1 | Arduino Uno (Rev3) | type Arduino UNO (Rev3)
Part2 | Adafruit Micro USB Breakout | variant variant 2; part # Adafruit #1833
PI Camera | IC | chip label IC; editable pin labels false; hole size 1.0mm,0.508mm; package DIP (Dual Inline) [THT]; pin spacing 300mil; pins 8; variant variant 6
Power Supply | DC Power Supply | internal resistance 0Ω; max current 14.6A; type dc; voltage 24V
Ring Light | LEDs | package led10mm; variant variant 1
USBTTL1 | USB A Plug | variant 1
USBTTL2 | USB B Plug | variant 2
X Axis | Stepper Motor - Unipolar | stepper type Unipolar
X limit switch | JL012-13-5.2 Lever (Limit) Switch SPDT + NO + NC | variant mini; part # JL012-13-5.2
Y Axis | Stepper Motor - Unipolar | stepper type Unipolar
Y limit switch | JL012-13-5.2 Lever (Limit) Switch SPDT + NO + NC | variant mini; part # JL012-13-5.2
Z Axis | Stepper Motor - Unipolar | stepper type Unipolar
Z limit switch | JL012-13-5.2 Lever (Limit) Switch SPDT + NO + NC | variant mini; part # JL012-13-5.2

## A.5 – BOM - Electronics

Table 8: Bill of Materials for electronics

Part Type | Properties | Amount
LM2596 step down module | Type LM2596 step down | 3
Raspberry Pi 5 | Processor Broadcom 2711, Quad-core Cortex-A76 64-bit SoC @ 2.4GHz; variant Raspberry Pi 5 | 1
Arduino_CNC_V3.00 | Variant 2 | 1
Arduino Uno (Rev3) | Type Arduino UNO (Rev3) | 1
Adafruit Micro USB Breakout | Variant 2; part # Adafruit #1833 | 1
Pi Camera | Chip label IC; editable pin labels false; hole size 1.0mm,0.508mm; package DIP (Dual Inline) [THT]; pin spacing 300mil; pins 8; variant 6 | 1
DC Power Supply | Internal resistance 0Ω; max current 14.6A; type dc; voltage 24V | 1
LEDs | Package led10mm; variant variant 1 | 1
USB A Plug | Variant 1 | 1
Micro USB B Plug | Variant 2 | 1
Stepper Motor - Unipolar | Stepper type Unipolar | 3
JL012-13-5.2 Lever (Limit) Switch SPDT + NO + NC | Variant mini; part # JL012-13-5.2 | 3

Optical Module Assembly Instructions Rev. 1, 09-Apr-2025

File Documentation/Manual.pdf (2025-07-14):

# MANUAL

# Optical Module

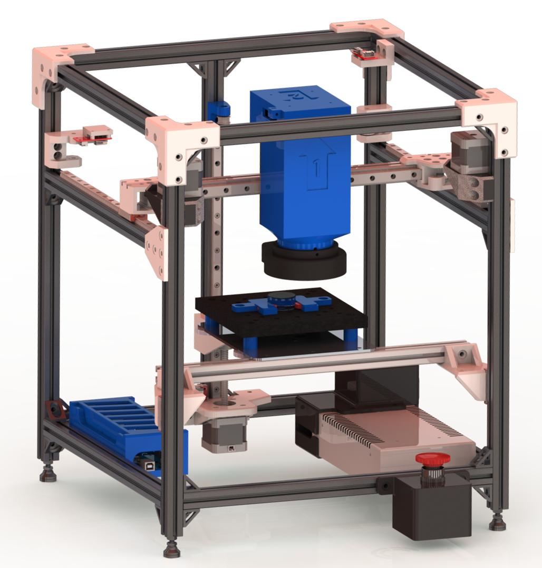
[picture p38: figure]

Optical Module Manual
Rev. 1, 09-Apr-2025

## Contents

1. Introduction | 4
2. Operation Instructions | 4
2.1 Quick Guide | 4
2.2 | Random Image Sampling | 6
2.3 | Scanning | 9
2.4 Platform Calibration Routine | 12
2.5 Other GUI Tabs | 13
2.5.1 Motion Tab | 13
2.5.2 Image Tab | 16
2.5.3 Details Tab | 18
2.6 Stage to Platform Matrix Transformation | 18
3. System Overview | 20
3.1 Structural Assembly | 20
3.2 Electrical Assembly | 21
3.3 Software Startup | 22
4. Maintenance | 23
4.1 Routine Maintenance | 23
4.2 Calibration Routines | 24
4.3 Equipment | 27
5. Safety | 28
5.1 Motors | 28
5.2 Electrical Wiring | 28
5.2.1 Power Supply | 28
5.2.2 Arduino and Converter Housing | 28

5.2.3 E-STOP | 28
6. FAQ | 29
7. Troubleshooting | 29

## 1. Introduction

This document is designed to explain how to use and maintain the functionality of the

optical module. The optical module was designed by a group of manufacturing

engineering students at the University of British Columbia (UBC) for their capstone

project as prescribed by Professor Ben Britton and PhD student Graeme Francolini.

The optical module is an automated optical microscope designed to function within Prof.

Britton’s self-driving lab for investigating metallurgical samples. The project is open-

source and the GitHub repository for the project can be found here:

https://github.com/ManuCapstone1/OpticalModule. For CAD modeling, BOM, STL files,

design documents, assembly documents and all pertaining programming files please

visit the GitHub repository.

This document is solely designed for instructions on calibration, maintenance, and how

to use the optical module.

## 2. Operation Instructions

## 2.1 Quick Guide

The default procedure of operation of the module is the following:

1. Start the GUI program
2. Click “Create a new sample” button
3. Enter sample parameters requested in the window (Figure 1):
A) Select one of the mount types. Initially, available mount types are “Puck” and

“Stub”.

B) Enter sample name.
C) Enter the starting sample height. This parameter defines how tall the sample
is. | The more accurate the measurement is, the better the quality of autofocus is
| going to be.

D) Enter sample layer height. This affects the height change after each round of

polishing to reduce the time it takes to autofocus.

E) Enter the bounding box for the sample. This is used to define the sample size

inside of a puck or on a stub.

F) Click “Ok” to complete the entry or “Cancel” to close the window without

saving the new sample parameters.

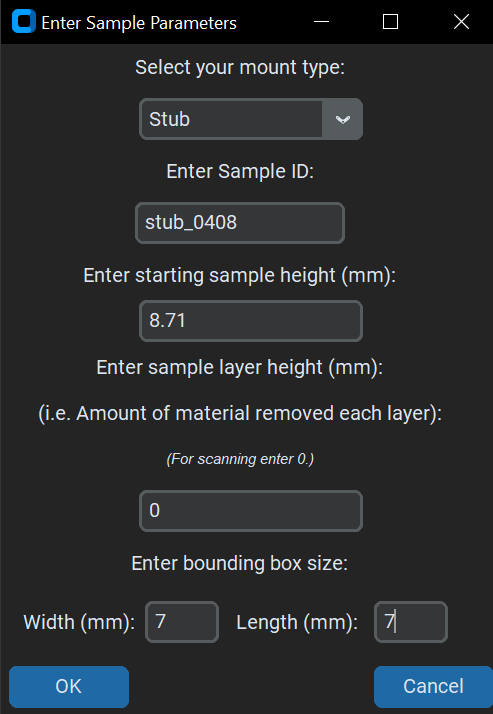
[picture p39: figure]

Figure 1 - Sample parameters pop-up window.

4. Select the desired mode of operation and click either “Random Sampling” or

“Scanning”. Check the “Random Image Sampling” or “Scanning” sections of the manual

for more information.

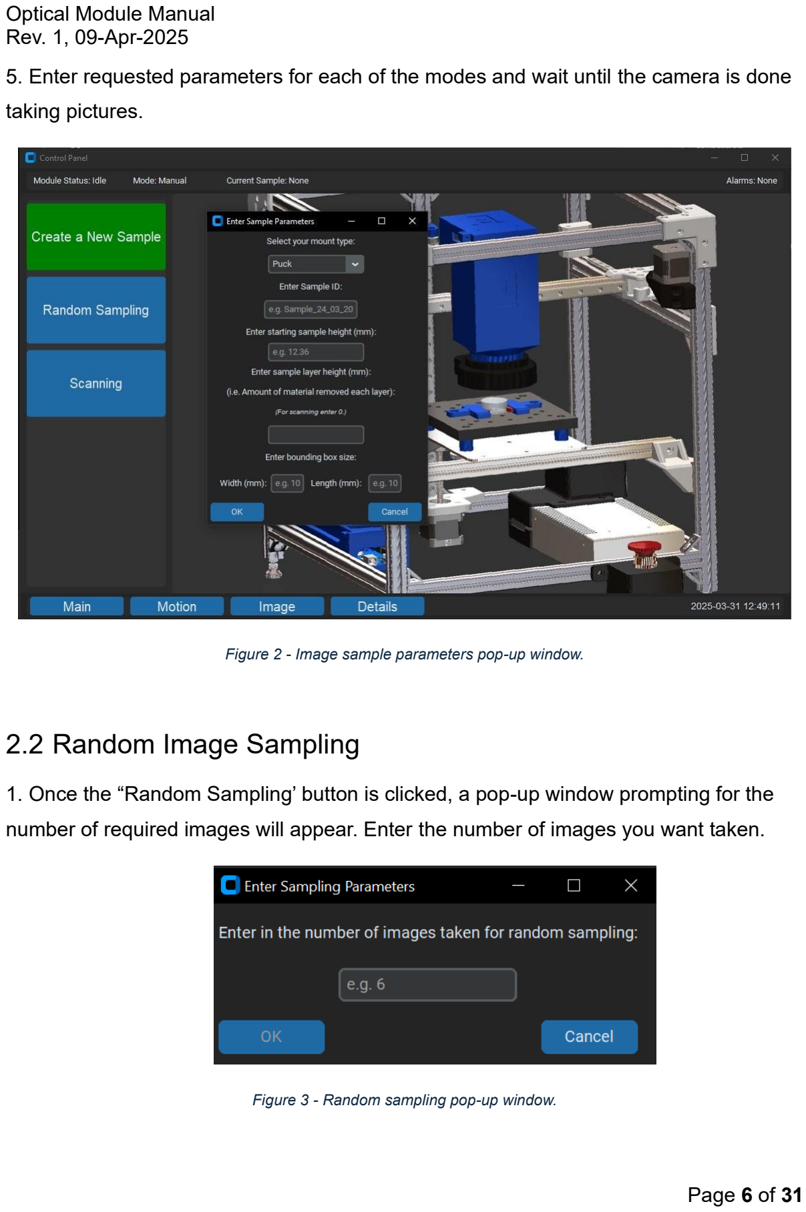
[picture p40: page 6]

5. Enter requested parameters for each of the modes and wait until the camera is done

taking pictures.

Figure 2 - Image sample parameters pop-up window.

## 2.2 Random Image Sampling

1. Once the “Random Sampling’ button is clicked, a pop-up window prompting for the

number of required images will appear. Enter the number of images you want taken.

Figure 3 - Random sampling pop-up window.

2. Then, a new loading screen in the right part of the window will appear. It indicates

that the camera is currently taking images. You can press “Stop” button to interrupt the

process at any point. This will require re-homing the system before you can restart the

task.

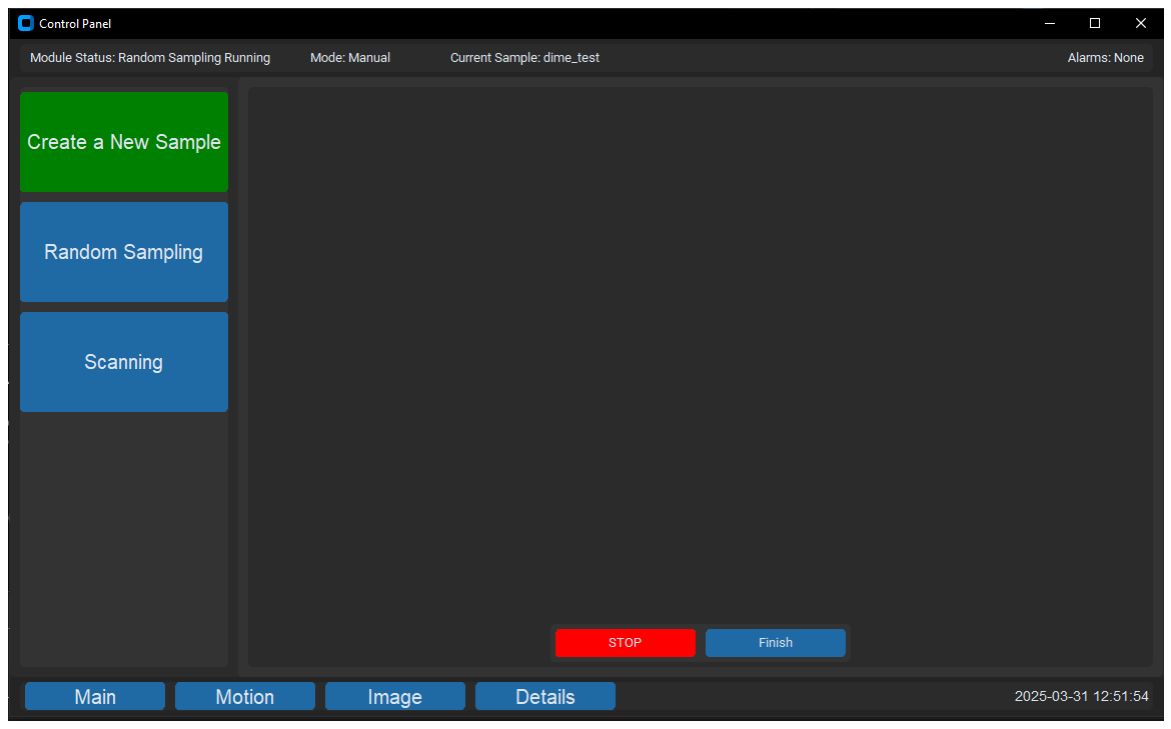
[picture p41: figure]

Figure 4 - Random sampling mode loading screen.

3. After the module is done taking images, a new screen with all images will be

displayed in the right part of the window. The images are stored in the directory

specified on the “Details” tab of GUI.

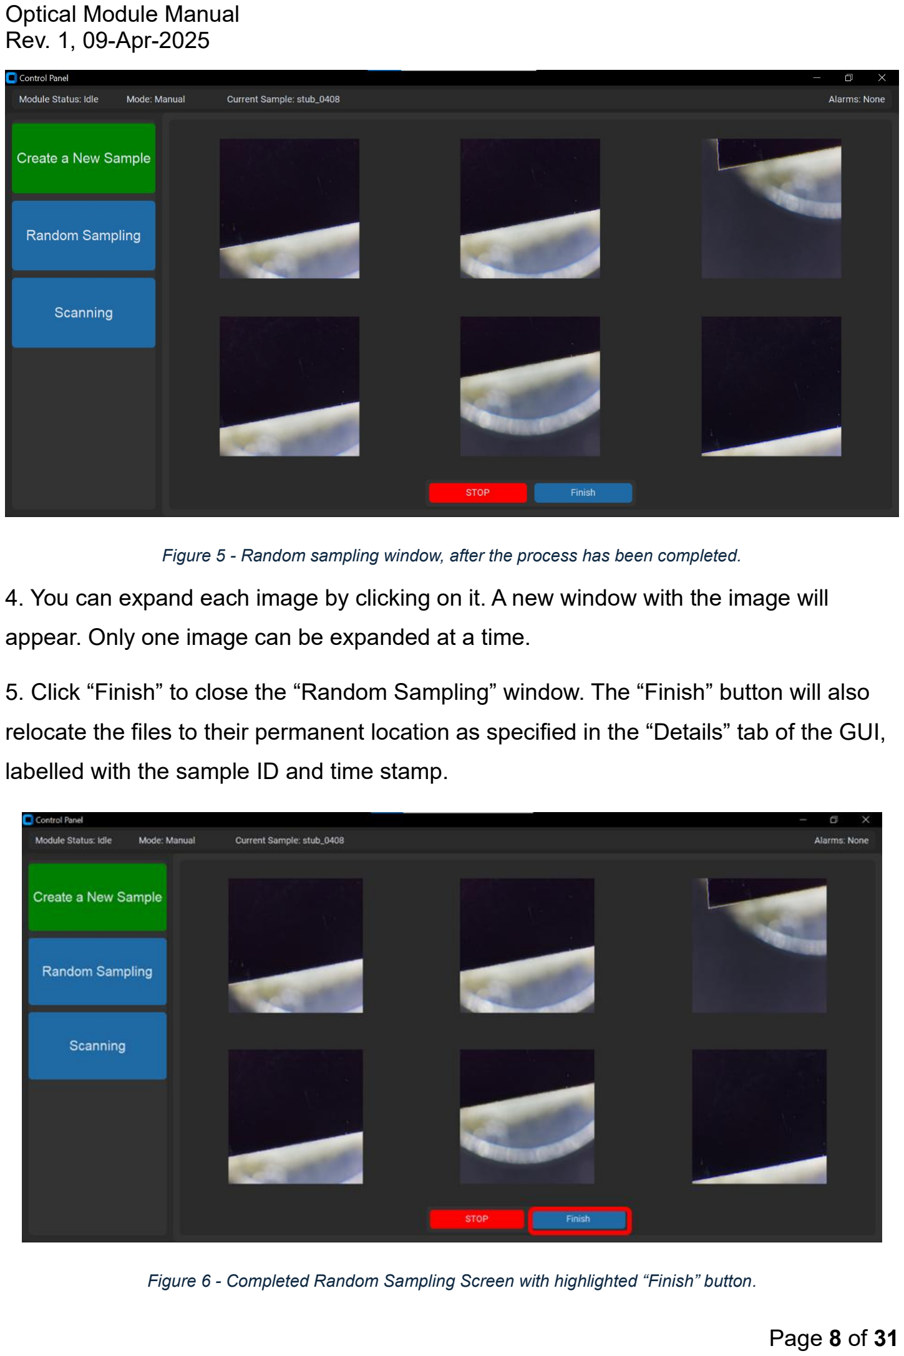
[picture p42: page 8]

Figure 5 - Random sampling window, after the process has been completed.

4. You can expand each image by clicking on it. A new window with the image will

appear. Only one image can be expanded at a time.

5. Click “Finish” to close the “Random Sampling” window. The “Finish” button will also

relocate the files to their permanent location as specified in the “Details” tab of the GUI,

labelled with the sample ID and time stamp.

Figure 6 - Completed Random Sampling Screen with highlighted “Finish” button.

## 2.3 Scanning

1. Once the “Scanning’ button is clicked, a pop-up window prompting for the sample

length and width. This would describe the bounding box around the sample to calculate

the number of images to be taken. Recommended parameters are 5 for X direction and

4 for Y direction.

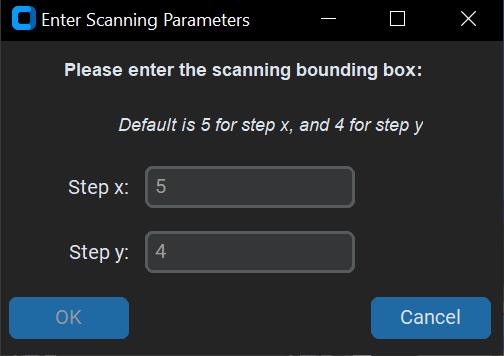
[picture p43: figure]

Figure 7 - Scanning parameters pop-up window.

2. Then, a new loading screen in the right part of the window will appear. It indicates

that the camera is currently taking images. You can press “Stop” button to interrupt the

process at any point. This will require re-homing the system before you can restart the

task.

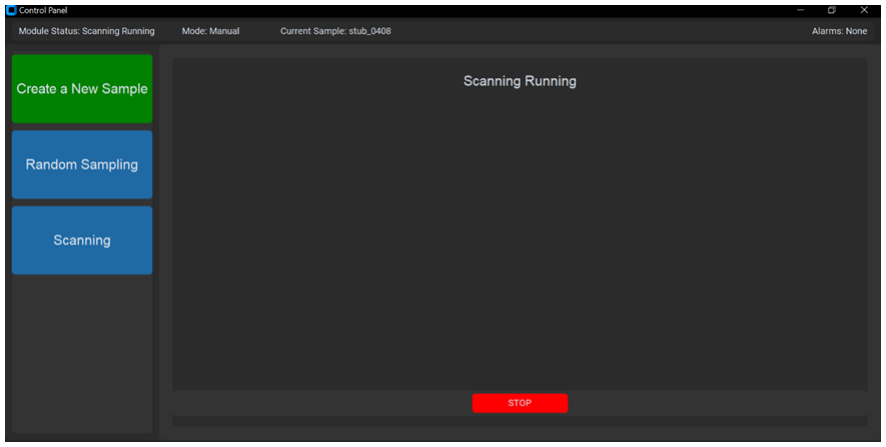
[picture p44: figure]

Figure 8 - Screenshot of GUI when scanning is in the process of running.

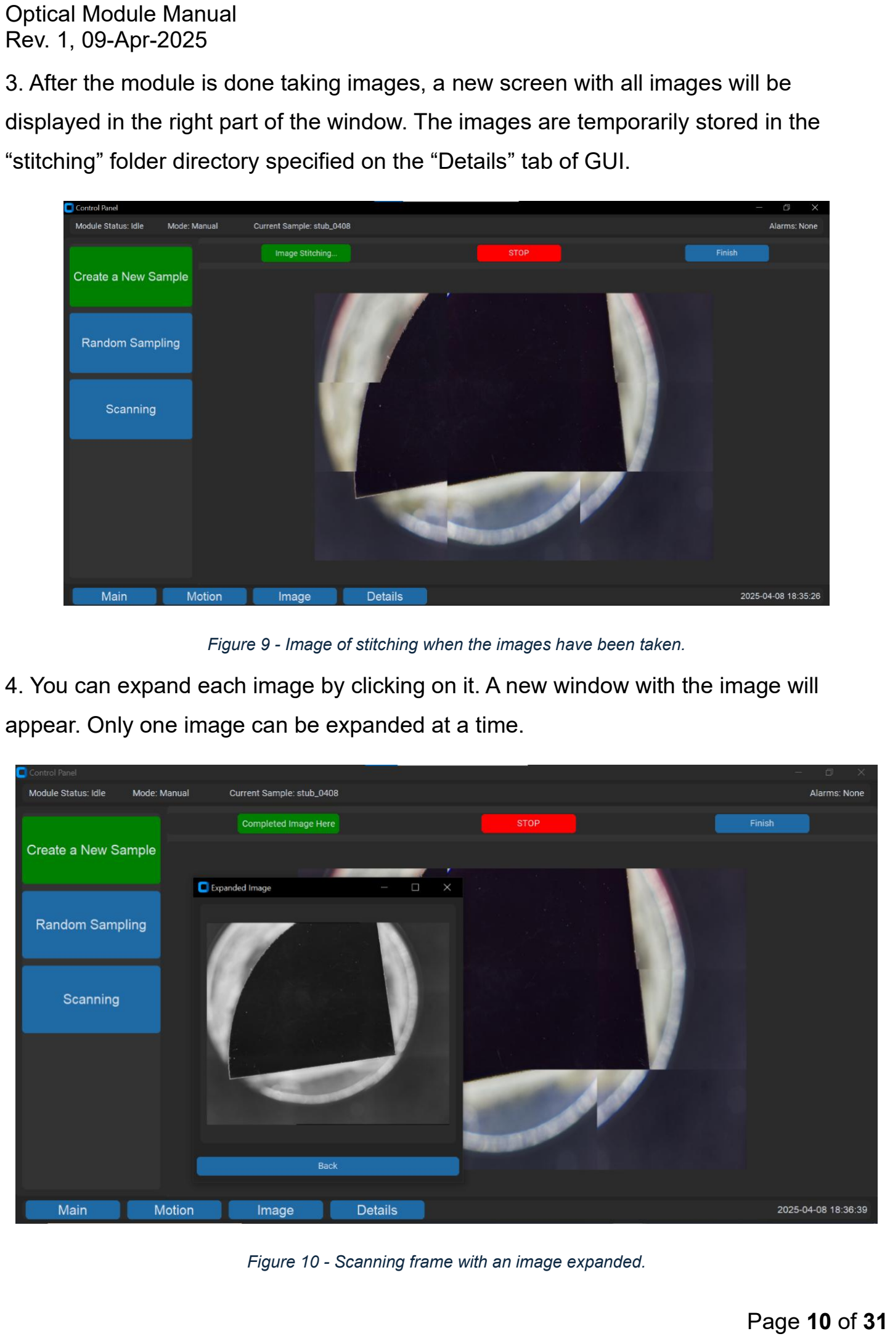
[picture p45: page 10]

3. After the module is done taking images, a new screen with all images will be

displayed in the right part of the window. The images are temporarily stored in the

“stitching” folder directory specified on the “Details” tab of GUI.

Figure 9 - Image of stitching when the images have been taken.

4. You can expand each image by clicking on it. A new window with the image will

appear. Only one image can be expanded at a time.

Figure 10 - Scanning frame with an image expanded.

5. Once the software had finished stitching the images together, a “Complete Image

Here” button will appear at the top left of the screen. It will display the complete stitched

image in a separate window that can be expanded. You can also access the stitched

image in the “stitching” folder as specified in the “Details” tab of the GUI.

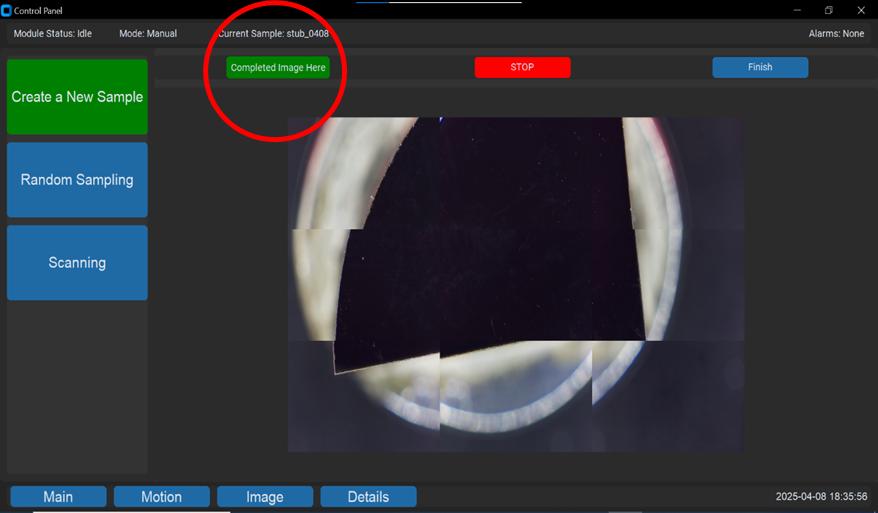
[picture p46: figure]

Figure 11 - Scanning completed, stitched image location circled in red.

6. Click “Finish” to close the “Scanning” window. Similar to Random Sampling, when the

“Finish” button is pressed, the PC will relocate the files to it’s permanent location as

specified in the “Details” tab of the GUI, labelled with the sample id and time stamp.

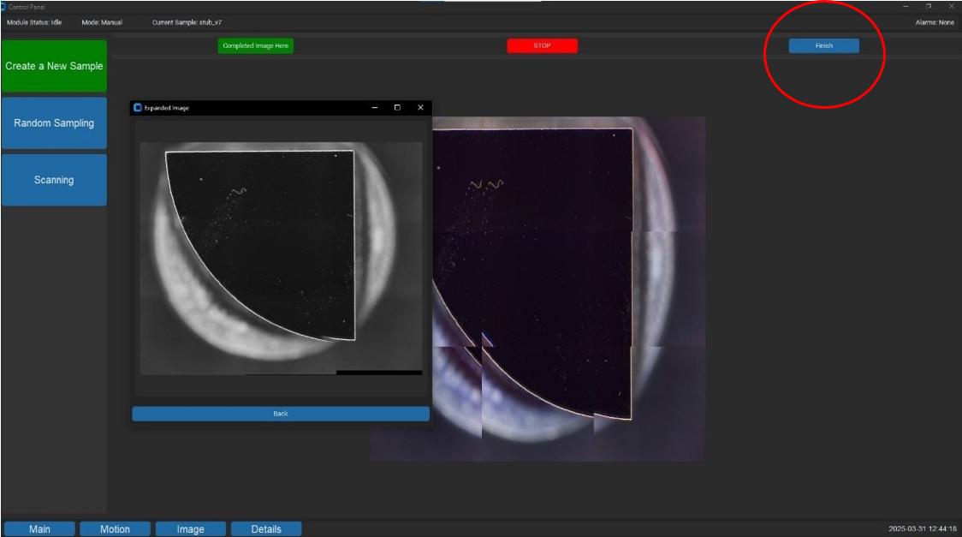
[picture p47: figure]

Figure 12 - Completed scanning process, with stitched image expanded.

## 2.4 Platform Calibration Routine

In order to ensure that all regions of the captured image remain consistently in focus, it

is essential that the platform is properly levelled. Variations in height across the surface

can lead to blurred or unfocused areas in the final image, especially at the corners.

Manual Platform Leveling:

The platform is supported at each of its four corners by height-adjustable knobs. These

knobs allow users to manually tune the z-height of each corner to achieve a level

imaging plane. The process involves incrementally adjusting each knob while observing

the focus at the corresponding corner.

Autofocus Support via Script:

Although an automatic "Calibrate Platform" button is not yet implemented in the GUI,

the foundation for this feature exists in the opticalModule.py script. A skeleton function

has been developed that performs the following steps:

- Moves the camera to each corner of the platform.
- Executes an autofocus routine centered on a crosshair marker in the field of

view.

- Records the z-height that achieves the best focus score at each corner.

This data can be used to guide manual adjustments. By comparing the optimal focus

height at each corner, users can determine which knobs to raise or lower to bring all

corners into alignment.

Camera Angle Considerations:

Ensure that the camera is mounted squarely to the platform. A tilted camera can lead to

uneven focus across the image, even if the platform itself is level.

Potential Future GUI Integration:

A dedicated "Calibrate Platform" button was added to the GUI and is currently

commented out in the gui.py script (see GitHub). This feature was initially planned to

run the autofocus routine for each corner automatically and display the corresponding z-

heights in the GUI.

## 2.5 Other GUI Tabs

2.5.1 Motion Tab

Motion Tab provides the user with the capability to adjust the position of the carriage.

Before you start any action on the motion tab, make sure that the system has been

homed and press “Refresh Coordinates” button. This will display the most recent

position of the carriage.

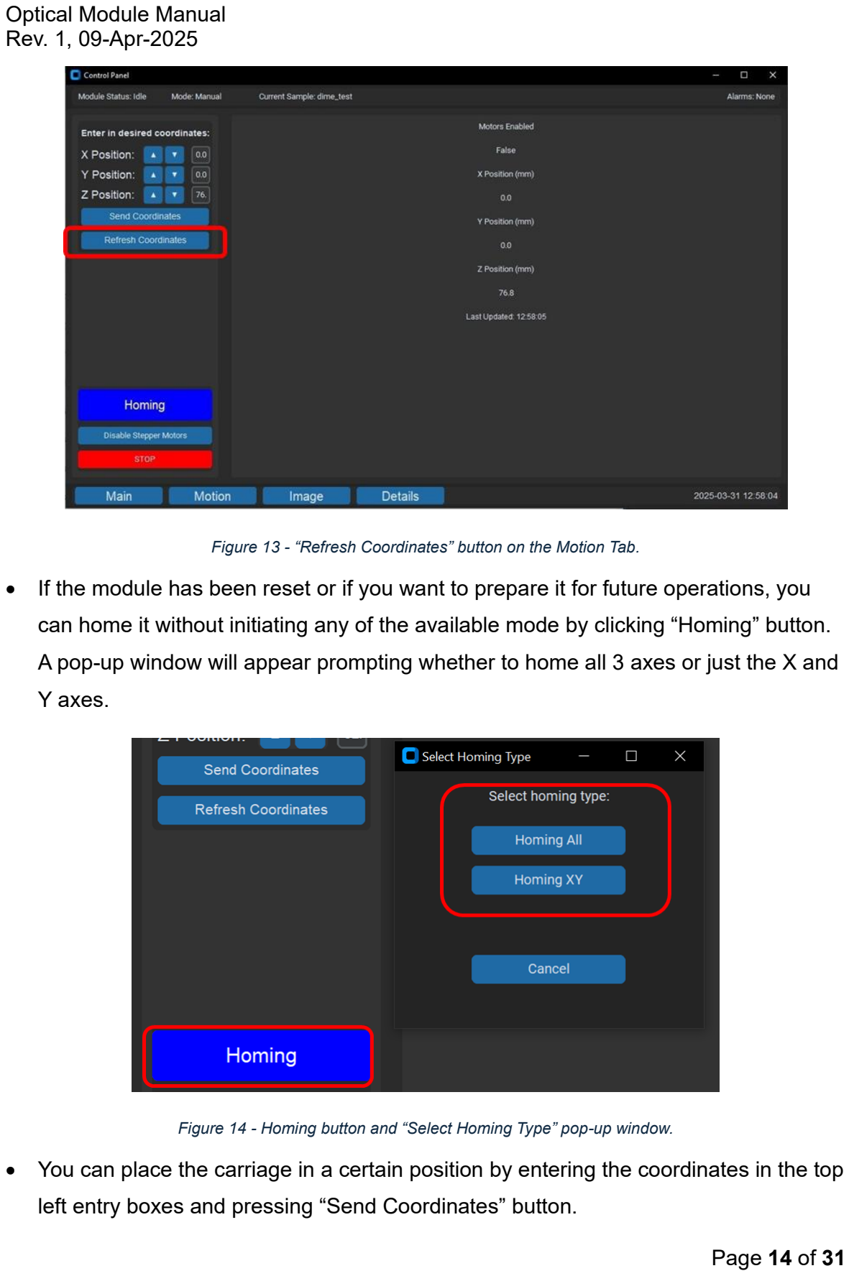
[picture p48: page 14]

Figure 13 - “Refresh Coordinates” button on the Motion Tab.

- If the module has been reset or if you want to prepare it for future operations, you

can home it without initiating any of the available mode by clicking “Homing” button.

A pop-up window will appear prompting whether to home all 3 axes or just the X and

Y axes.

Figure 14 - Homing button and “Select Homing Type” pop-up window.

- You can place the carriage in a certain position by entering the coordinates in the top

left entry boxes and pressing “Send Coordinates” button.

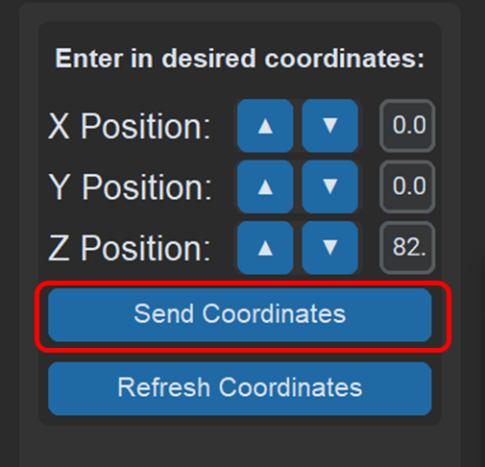
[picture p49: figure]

Figure 15 - “Send Coordinates” button on Motion Tab.

- You can also position the carriage in a particular location by pressing the “Disable

Stepper Motors” button and manually dragging the carriage to the desired position.

- *WARNING* At the time of completion of the project, only two out of three

motors (X and Y) are disabled by pressing the button. Use CAUTION while

moving the carriage manually.

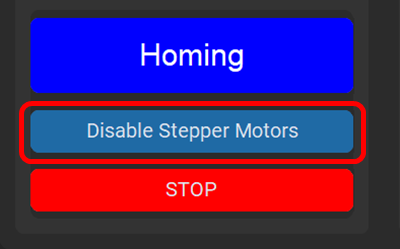
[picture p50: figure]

Figure 16 - “Disable Stepper Motors” button on the Motion Tab.

- You can press “Stop” button to interrupt any process at any point. This will require

re-homing the system before you can restart the task.

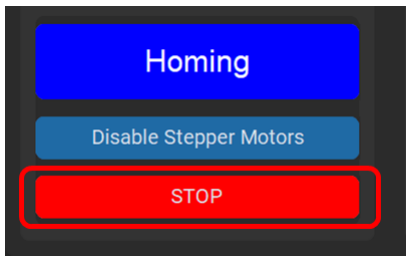
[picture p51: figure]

Figure 17 - “Stop” button on the Motion Tab to abort any operations.

2.5.2 Image Tab

Image Tab provides information on the current parameters used for the Raspberry Pi

camera and allows the user to take images of selected regions without running any of

the two modes of operation. Before you can adjust any camera parameters, please

press the “Refresh Data” to extract the most recent values for each of the parameters.

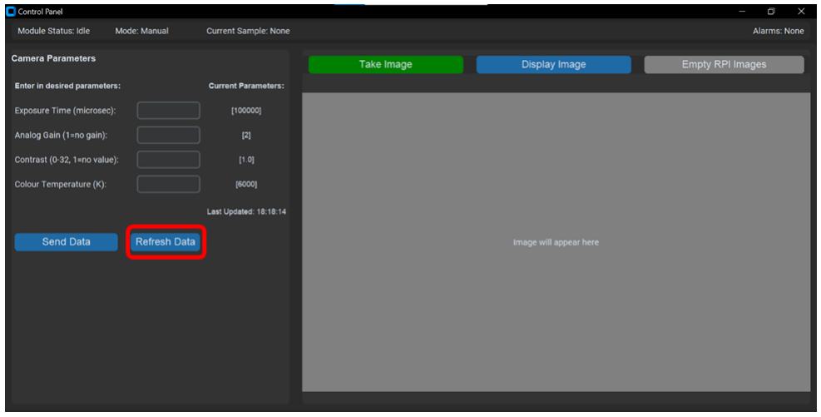
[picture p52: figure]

Figure 18 - “Refresh Data” button on the Image Tab without extracted image.

- You can adjust Raspberry Pi camera parameters by entering desired

parameters in the associated text box and clicking “Send Data” button. Click

“Refresh Data” after 5 seconds to ensure that the updated data has been

received by the camera.

- *WARNING* At the time of completion of this project, the Raspberry Pi

receives the new parameters successfully but does not update the

settings correctly.

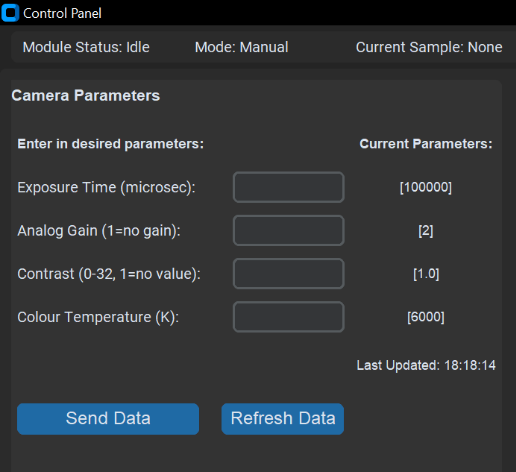
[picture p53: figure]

Figure 19 - Camera parameters update section on the Image Tab.

- After you position camera in the desired location, click “Take Image” button to

capture the image. Then, click “Display Image” to display the image in the

image window on the right side of the image tab.

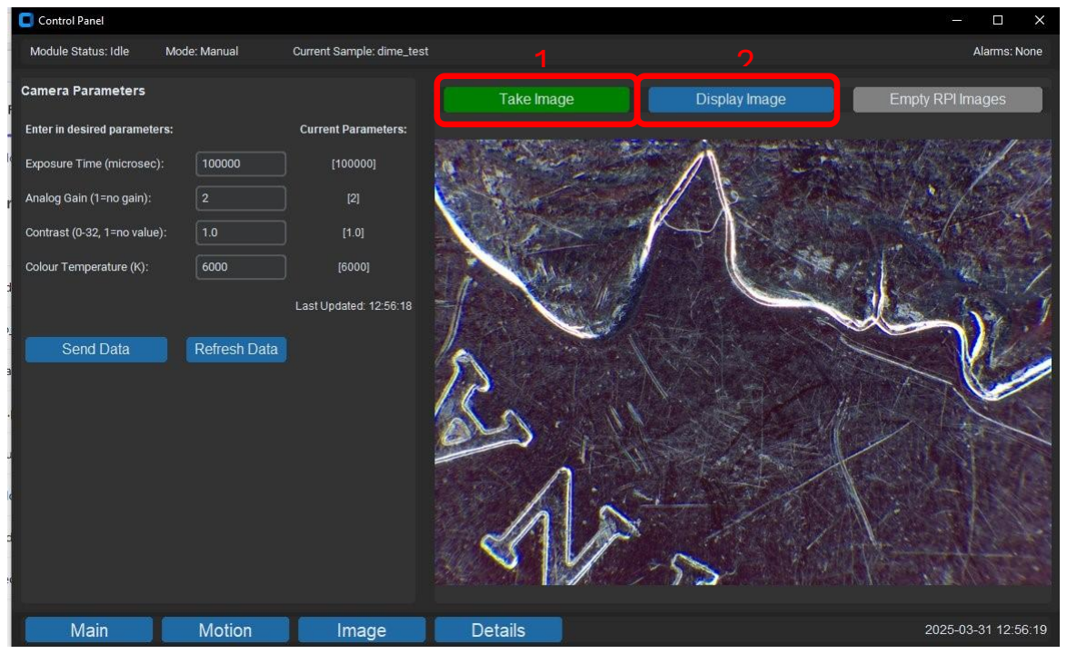
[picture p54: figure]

Figure 20 - Take Image” and “Display Image” buttons on the Image Tab with displayed image.

- To empty the folder that stores images on the Raspberry Pi, click “Empty RPI

Images” button. This should be done automatically in all current processes;

however, it can be used for troubleshooting.

Figure 21 - “Empty RPI Images“ button on the Image Tab.

2.5.3 Details Tab

Details Tab (Figure 22) includes some short information on how to use the program as

well as the information on the directories used to store files and images. To change any

folder paths, you must change them manually in the python file gui.py (link). (https://github.com/ManuCapstone1/OpticalModule/blob/main/Programming%20Files/pc_files/gui.py)

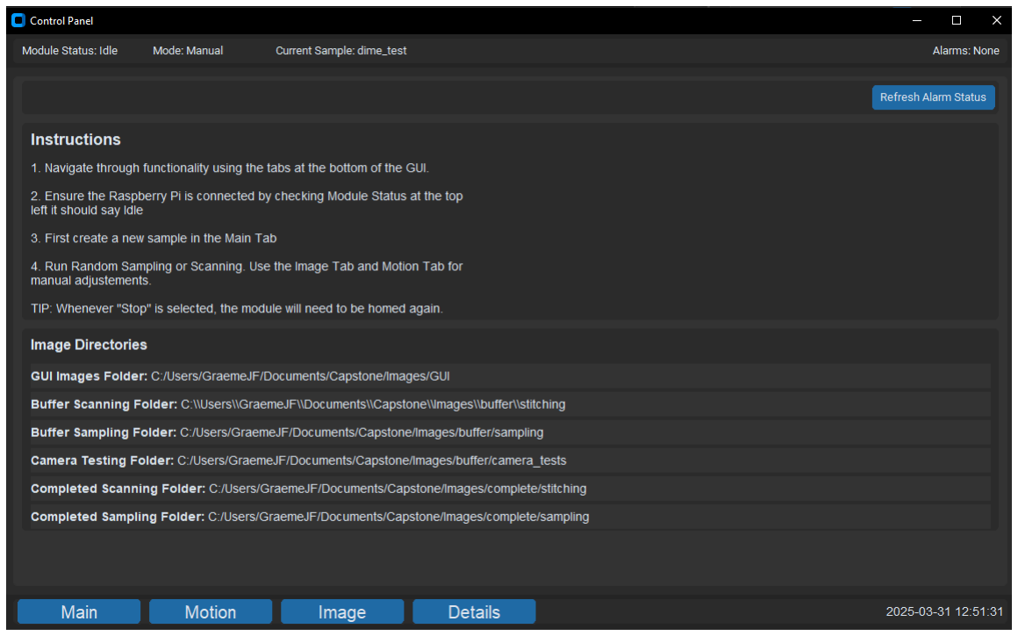
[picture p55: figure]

Figure 22 - "Details" tab on GUI.

## 2.6 Stage to Platform Matrix Transformation

This is an automatic method of establishing scaling and rotation aspects of affine

transformation, the method returns the transformation matrix. It is initially intended for

Click and Move feature for the microscope, but it is not implemented yet.

The method computes the affine transformation matrix by capturing images at stage

coordinates (49,28), (49,27), and (50,27). ORB features are extracted and matched

across images to identify a common point, which is used to estimate scaling and

rotation. Marked images are saved to the working directory as:

image1_x=49_y=28.jpg

image2_x=49_y=27.jpg

image3_x=50_y=27.jpg

This transformation maps stage movement to image coordinates, allowing spatial

calibration of the camera relative to the stage. The method can be found in

opticalmodule.py, under matrix_transform(self).

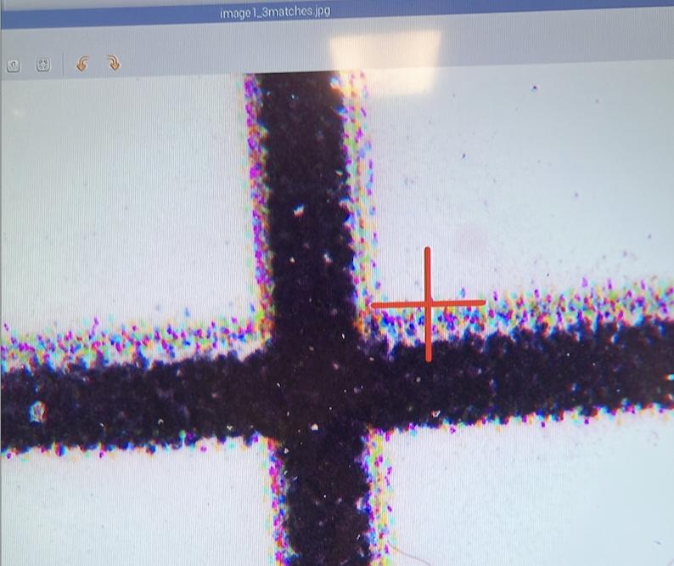
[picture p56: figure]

Figure 23 - The crosshair marker indicates the common feature amongst three images (locations).

## 3. System Overview

## 3.1 Structural Assembly

Figure 24 and Figure 25 and show the CAD renderings of the system's structural

assembly, with key components clearly labeled for user reference. The frame consists of

aluminum extrusions that support all functional modules of the system, ensuring rigidity

and alignment during operation.

Critical components are highlighted to assist users with system calibration, routine

maintenance, and safety awareness:

Users should familiarize themselves with these components prior to operating the

system to ensure safe and accurate use.

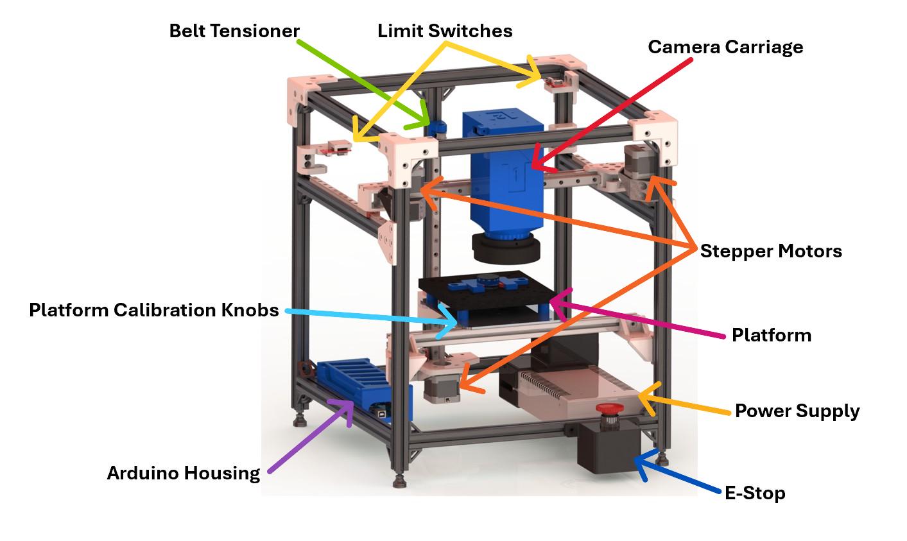
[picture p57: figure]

Figure 24 - Front View of the Structural Assembly.

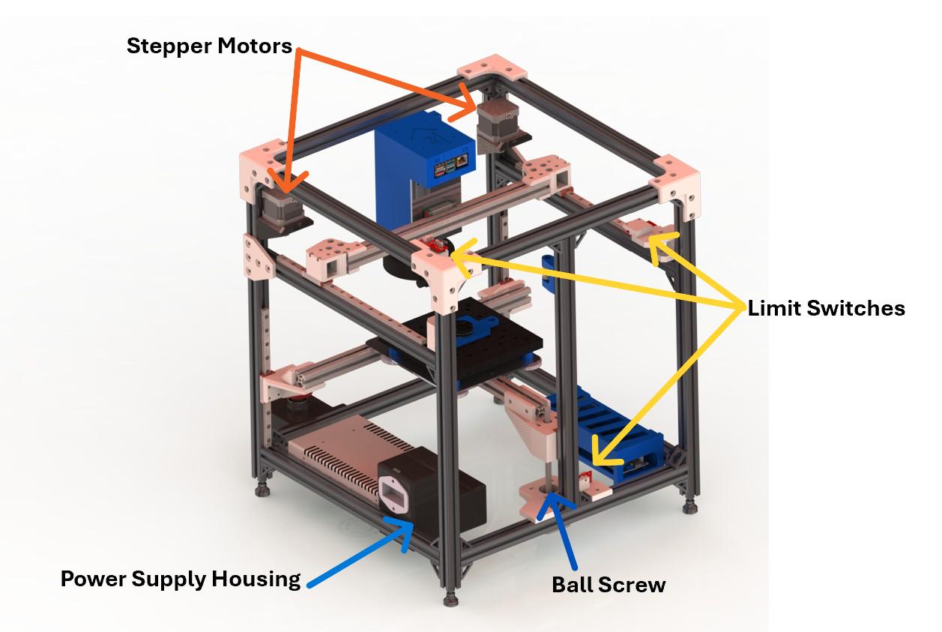
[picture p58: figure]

Figure 25 - Back View of the Structural Assembly

## 3.2 Electrical Assembly

### Figure 26 below shows a representation of the electrical components involved in this project. Since the power supply is rated at 24V and 14.6 A (Max), the voltage needs to be converted to 3 levels to accommodate the CNC shield (24V), ring light (12V) and Raspberry

Pi (5V), respectively. Furthermore, stepper motors and limit switches (NO) are connected to

### the CNC shield via their designated pins. An emergency stop is designed to cut off all power of the electrical system at the Live end of the AC power input. Arduino Uno is

powered by the Raspberry Pi via a serial connection (USB-A to USB-B). In addition, there is a STOP button on the PC GUI to stop all actions without turning the power off. It is used for

### quick testing while saving coordinates without the need for homing. Note that the AC

generator represents the 110V wall outlet and the power supply is not the exact model, but the same connection regardless.

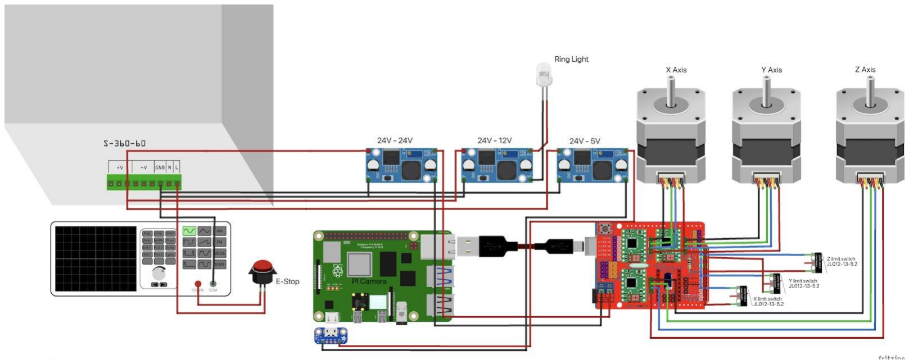
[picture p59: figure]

Figure 26 - Electrical component connections.

## 3.3 Software Startup

All programming files, and explanations can be found in the GitHub here. (https://github.com/ManuCapstone1/OpticalModule/tree/main) Before starting

up the software, ensure that the ethernet cable is plugged into both the Raspberry Pi

and the PC. To get into the Raspberry Pi’s interface, either connect the Raspberry Pi to

a monitor of it’s own or use RealVNC to remote into the Raspberry Pi.

To start the code of the Raspberry Pi, first setup the virtual environment by typing in the

following into the terminal:

source DIY_Eng_CV/bin/activate

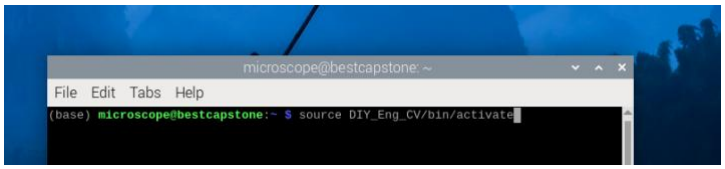
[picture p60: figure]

Figure 27 - Screenshot of setting up the virtual environment on the Raspberry Pi.

Then to start the code, start rpmain.py like so:

python rpmain.py

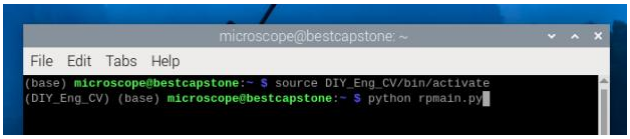
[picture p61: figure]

Figure 28 - Running rpmain.py on the Raspberry Pi.

To start the GUI, navigate to where the PC Files are in the PC with cd on the terminal.

Then run main.py.

python main.py

## 4. Maintenance

## 4.1 Routine Maintenance

To ensure optimal performance and longevity of the system, users should follow the

routine maintenance schedule outlined in Table 1. This table provides a clear

breakdown of each component, the maintenance task required, the recommended

frequency, and the procedure for completing the task. Regular inspection and servicing

of components such as the belt system, linear rails, bearings, fasteners, and electrical

connections help prevent unexpected failures and maintain calibration accuracy. Users

should refer to this table periodically and document completed tasks as part of their

maintenance log.

Table 1 - Routine maintenance schedule.

Component | Task | Frequency | Procedure
Belt System | Check belt tension | Every 30 days | Inspect for proper tension and adjust if loose.
| Replace belt if damaged | Every 90 days (or as needed) | Replace if frayed, cracked, or excessively loose.
Linear Rails & Bearings | Clean and lubricate linear rails | Every 60 days | Wipe debris, clean with isopropyl alcohol, apply PTFE dry lubricant.
| Clean and lubricate ball screw assembly | Every 90 days | Remove old lubricant, apply lithium/PTFE grease.
| Inspect bearings for wear | Every 180 days | Check for excessive play or grinding noise.
Fasteners & Structural Integrity | Check witness marks and re-tighten bolts | Every 60 days | Verify and re-tighten bolts in frame, optical module, platform, and rail assemblies.
Electrical Components | Inspect wiring connections | Every 90 days | Ensure stepper motor, limit switches, and power cables are securely connected.
| Check power supply & voltage regulators | Every 180 days | Confirm stable voltage output from the DC-DC converters.
| Test emergency stop functionality | Every 30 days | Press and release the E-stop switch to verify response.

## 4.2 Calibration Routines

To maintain system accuracy and imaging quality, Table 2 outlines the recommended

calibration routines for critical components. Each row details the specific calibration

task, how often it should be performed, and a general procedure. Regular calibration ensures that the platform remains level, the optical system produces sharp and properly

aligned images, and motion components such as the CoreXY system and Z-axis motor

maintain precise positioning. Users should refer to this table before critical operations or

if performance issues arise and follow each procedure carefully to ensure reliable

system function.

Table 2 - Calibration routines schedule.

Component | Task | Frequency | Procedure
Platform Leveling | Re-level the platform | Every 60 days (or before critical use)
1. Disable the motors, then
| | | manually move the camera carriage so it is positioned over the crosshair sticker in the bottom-left corner of the breadboard stage.
2. Capture an image using the Image tab.
| | | -If the image appears out of focus, manually adjust the height of the platform by rotating the lead screw. -Repeat the image capture and lead screw adjustment until the image is in clear focus.
3. Move on to the next corner in the
| | | counterclockwise direction and capture an image using the Image

tab.

| | | -If the image appears out of focus, manually adjust the knob for that

corner.
| | | -Repeat the image capture and knob adjustment until the image is in clear focus.
4. Repeat step 3 for two remaining
| | | corners, moving in a counterclockwise direction.
5. Ensure that all four corners are in
| | | focus by manually moving the camera over the cross hair and

capturing the image. If at least one of the corners appears to be out of focus – repeat steps 3 and 4.

Optical
Calibration

Check
microscope
focus &
alignment
Every 30 days | Capture an image of the sample or breadboard using the Image tab.
| -If one side of the image appears sharp while the opposite side is blurry, this may indicate a perpendicularity issue between the lens and the stage. -To correct this, adjust the knob screws supporting the bottom of the lens until the entire image is uniformly in focus.
| Note: Slight blurriness in the image corners is normal (spherical aberration) and does not necessarily indicate a perpendicularity issue.
| Clean the lens | Every 30 days | Use compressed air, microfiber cloth, and lens cleaning solution if necessary.
Motion System Calibration | Check CoreXY motion drift | Every 90 days | Move the camera carriage to a predefined position on the breadboard stage and verify the movement accuracy using a caliper: -For example, move the carriage 50 mm in the X-direction. -Measure the initial distance between the side of the carriage and the aluminum extrusion. -After the move, measure the final distance—it should reflect the expected 50 mm shift. If there is a discrepancy between the expected and actual movement, perform maintenance on the Belt System to correct the issue.

Z-axis DC
Motor drift
check

Every 90 days
(or if accuracy
issues arise)

Move the platform to a predefined position along the Z-axis and verify the movement accuracy using a caliper:
-For example, move the platform 20 mm upward.
-Measure the initial distance between the platform and the lead screw bracket.
- After the move, measure the final distance, it should reflect the expected 20 mm shift.

If there is a discrepancy between the expected and actual movement, perform maintenance on the Linear Rails and Bearing system to correct the issue.

## 4.3 Equipment

Table 3 lists parts and materials that will need to be purchased somewhat regularly to

upkeep and maintain the optical module.

Table 3 - List of parts that will be regularly purchased.

Part | Specifications/Notes | Approximate Cost (CAD)
Linear Rail Lubricant | PTFE Dry lubricant or Superlube | $15 - $25
Ball Screw Lubricant | Super Lube 92003 Silicone Lubricating Grease with PTFE or Lucas Oil 10533 White Lithium Grease | $15 - $35
Belt | GT2, 6mm wide timing belt. ~1m long. | $15 - $35
Isopropyl Alcohol | | $5 - $20

## 5. Safety

## 5.1 Motors

There are three stepper motors in use for the optical module. The motors get hot after

some time. Avoid touching the motors when enabled, or when the device has been on

for more than 10 minutes.

Furthermore, avoid entering within the confines of the frame when the optical module is

in use to avoid any pinch points. Use the E-Stop immediately if any complications occur.

Lastly, don’t have any loose hair, clothing, or jewelry near stepper motors and belts

when the device is enables.

## 5.2 Electrical Wiring

5.2.1 Power Supply

If making any modifications to the power supply housing, ensure that the optical module

is unplugged from the outlet, and that the power supply has been off for about five

seconds at least. The power supply stores energy in very large capacitors, so the

energy does not dissipate immediately.

5.2.2 Arduino and Converter Housing

Do not make any modifications to the housing for the converters or Arduino when the

system is running or has power. This could cause adverse affects to the motors,

Raspberry Pi, and overall software. Furthermore, although the electric current and

voltage is low, it is inadvisable to make any modifications when the system is running

due to electrical safety concerns.

5.2.3 E-STOP

The optical module is equipped with an E-STOP with is wired between the AC outlet and

DC power supply. When the E-STOP is pressed, any electrical current is mechanically stopped from flowing to the power supply. Warning: the DC power supply is equipped

with large capacitors, meaning that even after the E-STOP is pressed, the energy won’t

fully dissipate for a few seconds.

## 6. FAQ

Why won’t an old alarm go away?

Alarms are not automatically refreshed. To erase an old alarm, navigate to the details

tab and select “Refresh Alarm”.

Where do the images I take go?

During the process for both sampling and scanning, images are saved to a “Buffer”

folder. Then when the “Finish” button is selected, all the files are placed in a new folder

under the “complete” folder, with the folder labelled with the sample id and time stamp.

For specific folder paths, reference the “Details” tab on the GUI.

To change the folder path directories, they most be modified in the gui.py python file

(link). (https://github.com/ManuCapstone1/OpticalModule/blob/main/Programming%20Files/pc_files/gui.py)

Why is the Z-axis leadscrew making inconsistent noise?

Z-axis leadscrew may be misaligned. By visual inspection, one can determine the

deviation when turning the leadscrew (when power is off). Alternatively, the leadscrew

may be more difficult to turn at the very top. The solution would be to adjust the stepper

motor screws within the sliding screw holes on the motor bracket and continue the test

until the leadscrew is aligned with consistent torque throughout its length.

## 7. Troubleshooting

Why is the program crashing as soon as I send data?

If the program is crashing when trying to use GoTo, Create a New Sample, or Take

Image right after opening the GUI, this is an indication that the Raspberry Pi is not

receiving information.

First check the Module State in the top left corner. If the status is “Raspberry Pi is Not

Connected” this confirms the Raspberry Pi is not communicating with the Gui.

Second, ensure that the Raspberry Pi has power. Third, close the GUI, and then try

opening it again. Check to see if the Module State is still “Raspberry Pi is Not

Connected” or updated to “Idle”. Lastly, cut power to the optical module, and then power

it on again.

Why is my image blurry?

For the scanning function, the entered in “Layer Height” must be set to 0.

For the sampling function, ensure that the initial layer height is correct.

If neither of these solutions work, consider re-leveling the platform using the knobs

underneath and the three screws aligning the lens within the camera carriage.

Why is the GUI crashing when I’m stitching an image?

The program that runs image stitching, Fiji, requires a lot of RAM. If there are too many

images to stitch, this could cause the PC to max out it’s RAM and crash the system (e.g.

50+ images). Please enter a smaller width and height in the “Create New Sample”

dialog if this occurs.

Raspberry Pi is not starting up.

It could be the voltage supply of the buck converters. While the rated voltage for

raspberry pi is 5.1 V, sometimes it spikes to above 5V triggering built in protection. It is

advisable to turn the converter to less than 5V. If adjusting the converter fails, try

powering the Raspberry Pi with a separate USB-C charger.

Why is the Raspberry Pi not connecting to Wifi?

The Raspberry Pi will not be able to connect to a wifi network if it is currently connected

via ethernet to the PC. In order to access a wifi network, you must unplug the Ethernet

cable.

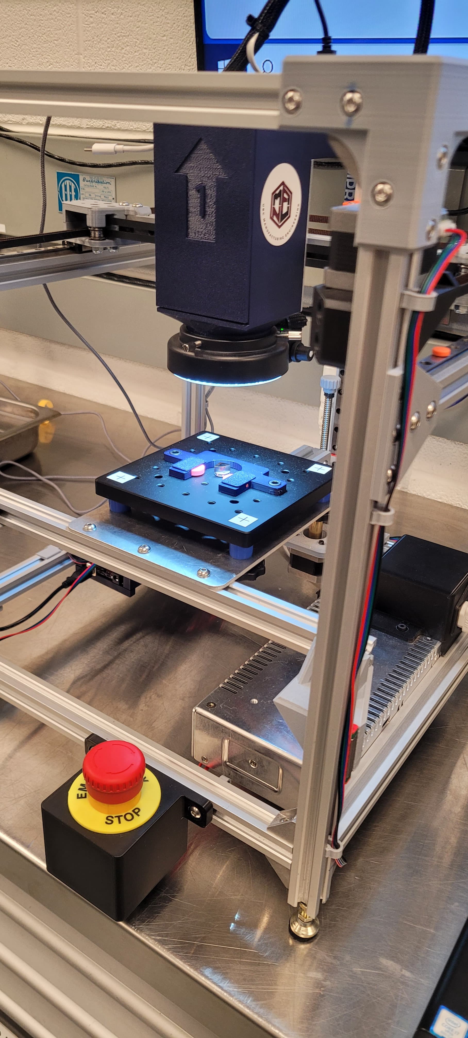
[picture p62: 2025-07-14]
Images/Picture/assembly_sideview_2.jpg

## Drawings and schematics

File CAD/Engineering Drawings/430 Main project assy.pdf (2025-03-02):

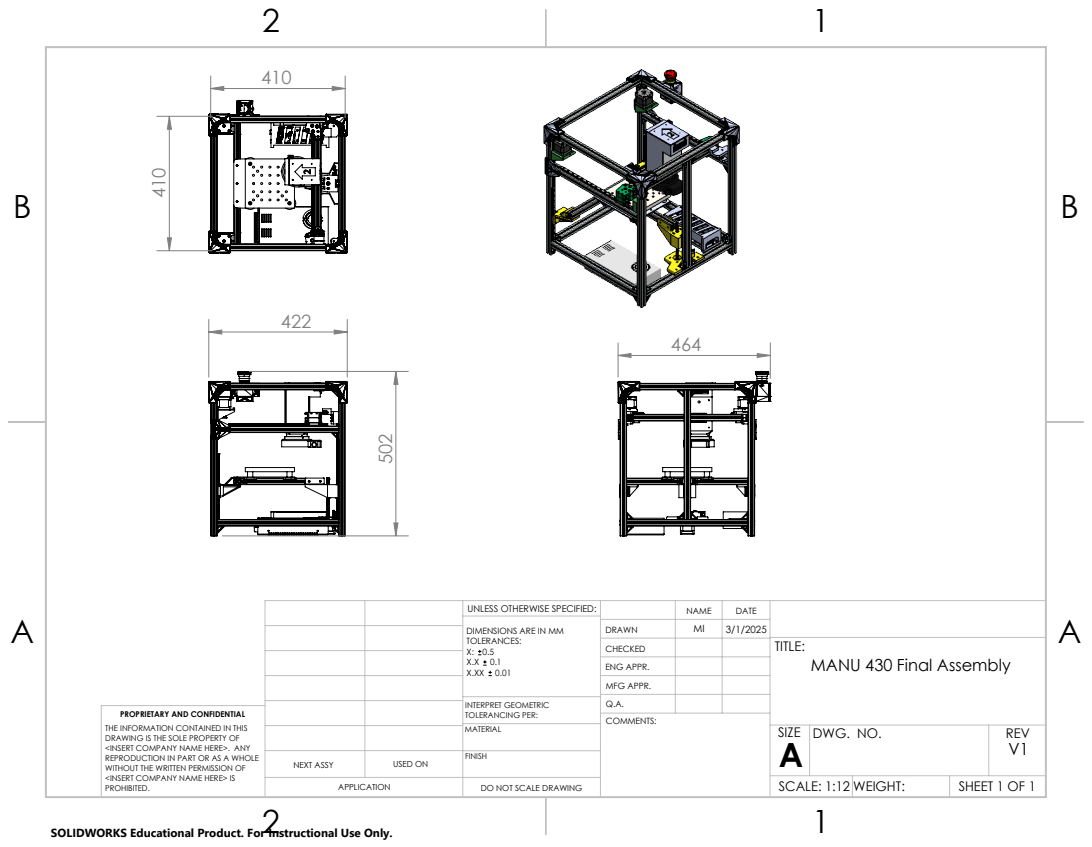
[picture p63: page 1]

UNLESS OTHERWISE SPECIFIED: | | NAME | DATE
DIMENSIONS ARE IN MM TOLERANCES: X: 0.5 X.X 0.1 X.XX 0.01 | DRAWN | MI | 3/1/2025

CHECKED | | | TITLE: MANU 430 Final Assembly

ENG APPR.
MFG APPR.

INTERPRET GEOMETRIC TOLERANCING PER: | Q.A.
MATERIAL | | SIZE A | DWG. NO. | REV V1

PROPRIETARY AND CONFIDENTIAL
THE INFORMATION CONTAINED IN THIS
DRAWING IS THE SOLE PROPERTY OF
<INSERT COMPANY NAME HERE>. ANY
REPRODUCTION IN PART OR AS A WHOLE
WITHOUT THE WRITTEN PERMISSION OF
<INSERT COMPANY NAME HERE> IS
PROHIBITED.

NEXT ASSY | USED ON | FINISH

APPLICATION | DO NOT SCALE DRAWING | | SCALE: 1:12 WEIGHT: | | SHEET 1 OF 1

SOLIDWORKS Educational Product. For Instructional Use Only.

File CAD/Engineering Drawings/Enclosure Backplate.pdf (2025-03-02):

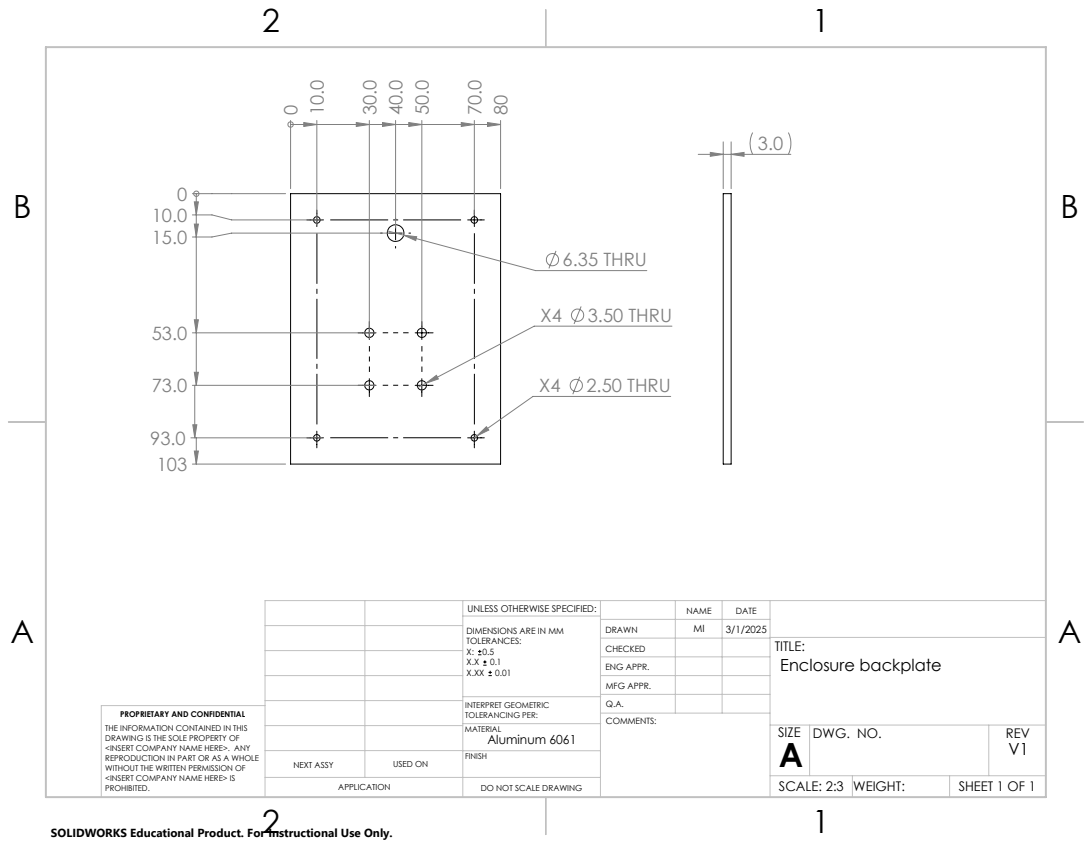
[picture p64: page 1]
X4 2.50 THRU; X4 3.50 THRU; 6.35 THRU

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

CHECKED | | | TITLE: Enclosure backplate

ENG APPR.
MFG APPR.

INTERPRET GEOMETRIC TOLERANCING PER: | Q.A.
MATERIAL Aluminum 6061 | | SIZE A | DWG. NO. | REV V1

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

NEXT ASSY | USED ON | FINISH

APPLICATION | DO NOT SCALE DRAWING | | SCALE: 2:3 | WEIGHT: | SHEET 1 OF 1

SOLIDWORKS Educational Product. For Instructional Use Only.

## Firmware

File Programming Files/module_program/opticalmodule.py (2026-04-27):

import pyfirmata
import time
import math
import cv2
import numpy as np
from picamera2 import Picamera2, Preview
import threading
import os
import random
import json

# Constants
STEPDISTXY = 0.212058/16 # linear distance moved in x and y each motor step (using 1/16 microstepping)
STEPDISTZ = 0.01/4 # linear distance moved in z each motor step (using 1/4 microstepping)
PULSEWIDTH = 100 / 1000000.0 # microseconds
BTWNSTEPS = 1000 / 1000000.0
STAGEFOCUSHEIGHT = 36860*STEPDISTZ # z height at which the stage is in focus (this may change with calibration)
STAGECENTRE = (8281, 7005) # Stage centre location in steps

class OpticalModule:
    """
        This class is a digital representation of the physical system. 
        It includes fields for the system parameters and methods for operating the system.
        Attributes:
            board: Pyfirmata Arduino board object
            enPin: Arduino pin used to enable and disable motors
            motorA (StepperMotor): Upper left stepper motor when viewed from the front
            motorB (StepperMotor): Upper right stepper motor when viewed from the front
            motorZ (StepperMotor): Motor connected to ball screw
            limitSwitchX (LimitSwitch): Limit switch for x-axis (back right corner)
            limitSwitchY (LimitSwitch): Limit switch for y-axis (back left corner)
            limitSwitchZ (LimitSwitch): Limit switch for z-axis (z motor bracket)
            cam (Camera): Camera object containing camera methods and attributes
            currX (int): Current x position of the camera carriage in steps
            currY (int): Current y position of the camera carriage in steps
            currZ (int): Current z position of the stage in steps
            currSample (Sample): Current sample in the system - this may be replaced with a list in the future for use with multiple samples
            totalImages (int): Total number of images to be captured in the current operation
            currImageMetadata: System parameters to be saved when an image is captured
            bufferDir (str): Directory where images are saved to be transferred to the PC
            alarmStatus (str): Alarm status to be displayed in the GUI
            positionLock (threading.Lock): Thread lock for updating or reading current position
            imageCountLock (threading.Lock): Thread lock for updating or reading image count information
            alarmLock (threading.Lock): Thread lock for updating or reading alarmStatus
            stop (threading.Event): Threading event used to indicate stop requested
            resetIdle (threading.Event): Threading event used to indicate that the module status should be reset to "Idle"
            isHomed (threading.Event): Threading event set when the system is homed; cleared if system is stopped or motors disabled
            motorsEnabled (threading.Event): Threading event to indicate whether motors are enabled

    """
    def __init__(self):

        # Instantiate pyfirmata Arduino board and iterator which allows limit switches to work
        self.board=pyfirmata.Arduino("/dev/ttyUSB0")
        it = pyfirmata.util.Iterator(self.board)
        it.start()
        
        # Set up enable pin to allow us to enable and disable motors for manual movement
        self.enPin = self.board.get_pin('d:8:o') 
        self.enPin.write(0)

        # Instantiate motor objects for the three motors. Motors A&B function according to CoreXY (see corexy.com for details)
        self.motorA = StepperMotor(2, 5, self.board)
        self.motorB = StepperMotor(3, 6, self.board)
        self.motorZ = StepperMotor(4, 7, self.board)
        
        # Instantiate limit switch objects
        self.limitSwitchX = LimitSwitch(9, self.board)
        self.limitSwitchY = LimitSwitch(10, self.board)
        self.limitSwitchZ = LimitSwitch(11, self.board)

        # Instantiate Camera
        self.cam = Camera()

        # Create variables to hold current position in terms of steps
        self.currX = 0 
        self.currY = 0
        self.currZ = 0
        self.currSample = None

        # Image variables
        self.totalImages = 0
        self.currImageMetadata = {
            "image_name" : "None",
            "sample_id" : "None",
            "timestamp" : time.strftime("%Y%m%d_%H%M%S"),  # Format: YYYYMMDD_HHMMSS
            "sample_layer" : 0,
            "image_number" : 0,
            "image_x_pos" : 0,
            "image_y_pos" : 0,
            "image_z_pos" : 0,
            "exposure_time" : self.cam.currExposureTime,
            "analog_gain" : self.cam.currAnalogGain,
            "contrast" : self.cam.currContrast,
            "colour_temp" : self.cam.currColourTemp
        }


        self.bufferDir = "/home/microscope/image_buffer"
        self.alarmStatus = "None"

        # Threading locks and events
        self.positionLock = threading.Lock()
        self.imageCountLock = threading.Lock()
        self.alarmLock = threading.Lock()
        self.stop = threading.Event()
        self.resetIdle = threading.Event()
        self.isHomed = threading.Event()
        self.motorsEnabled = threading.Event()

    def add_sample(self, mountType, sampleID, initialHeight, mmPerLayer, width, height):
        """
        Instantiates new sample and holds it as self.currSample
        Parameters:
            mountType: eg. puck or stub
            sampleID: User defined name for the current sample
            initialHeight: The initial z height of the sample in mm - how far above the stage is the surface of the sample
            mmPerLayer: Sample height reduction in each polishing step (in mm)
            width: Bounding box width in mm (x-direction)
            height Bounding box height in mm (y-direction)
        """
        self.currSample = Sample(mountType, sampleID, initialHeight, mmPerLayer, width, height)

    def disable_motors(self):
        """
        Disables stepper motors to allow for manual adjustment (system must run homing after)
        """
        self.enPin.write(1)
        self.motorsEnabled.clear() # motors not enabled
        self.isHomed.clear() # system not homed

    def enable_motors(self):
        """
        Enables stepper motors for continued use
        """
        self.enPin.write(0)
        self.motorsEnabled.set() # motors are enabled

    def _move_ab(self, deltaA: int, deltaB: int):
        """
        Internal method for moving the carriage in x and y

        Parameters:
            deltaA: How far and which direction to move motor A in steps
            deltaB: How far and which direction to move motor B in steps        
        """
        # Total number of steps to move the motors
        # Because we are only moving in cartesian directions the number of steps by each motor will always be the same
        # This may need to be changed in the future if diagonal or circular motion is required
        steps = abs(deltaA)

        # Set the direction of motors A and B
        if deltaA >= 0:
            self.motorA.dir_pin.write(1)
        else:
            self.motorA.dir_pin.write(0)

        if deltaB >= 0:
            self.motorB.dir_pin.write(1)
        else:
            self.motorB.dir_pin.write(0)

        # Move the motors the required number of steps
        for i in range(steps):
            # Stop system if stop is requested
            if self.stop.is_set():
                self.resetIdle.set()
                self.isHomed.clear()
                return
            self.motorA.step_pin.write(1)
            self.motorB.step_pin.write(1)
            time.sleep(PULSEWIDTH)
            self.motorA.step_pin.write(0)
            self.motorB.step_pin.write(0)
            time.sleep(BTWNSTEPS)


    def move_x(self, deltaX=0):
        """
        Move system in the x-direction
        Parameters:
            deltaX: Distance to move in x-direction (in steps)
        """
        # Determine distance and direction to move each motor (based on CoreXY)
        deltaA = -deltaX
        deltaB = -deltaX

        # Update current position
        with self.positionLock:
            self.currX = self.currX + deltaX 
        
        # Move motors
        self._move_ab(deltaA, deltaB)

    # Moves carriage in y by a given linear distance (mm)
    def move_y(self,deltaY=0):
        """
        Move system in the y-direction
        Parameters:
            deltaY: Distance to move in y-direction (in steps)
        """
        # Determine distance and direction to move each motor (based on CoreXY)
        deltaA = -deltaY
        deltaB = deltaY

        # Update current position
        with self.positionLock:
            self.currY = self.currY + deltaY
        
        # Move motors
        self._move_ab(deltaA, deltaB)

    def move_z(self, deltaZ=0):
        """
        Move platform in z-direction
        Parameters:
            deltaZ: distance to move in the z-direction (in steps)
        """
        # Find number of steps to move
        steps = abs(deltaZ)

        # Update current z-position
        with self.positionLock:
            self.currZ = self.currZ + deltaZ
        
        # Establish motion direction of motors
        if deltaZ >= 0:
            self.motorZ.dir_pin.write(1)
        else:
            self.motorZ.dir_pin.write(0)

        # Move z motor by specified number of steps
        for i in range(steps):
            # Stop motion if stop is requested
            if self.stop.is_set():
                self.resetIdle.set()
                self.isHomed.clear()
                return
            self.motorZ.step_pin.write(1)
            time.sleep(PULSEWIDTH)
            self.motorZ.step_pin.write(0)
            time.sleep(BTWNSTEPS)
    
    def go_to(self, x=None, y=None, z=None):
        """
        Moves system to specified (x, y, z) position (in mm)
        Parameters:
            x: x position relative to homed position (mm)
            y: y position relative to homed position (mm)
            z: z position relative to homed position (mm)
        """
        # If mm values are passed system calculates steps. If not remains at current position
        x = round(x/STEPDISTXY) if x is not None else self.currX
        y = round(y/STEPDISTXY) if y is not None else self.currY
        z = round(z/STEPDISTZ) if z is not None else self.currZ
        
        # If new values are passed move to specified position
        if not x == self.currX:
            self.move_x(x-self.currX)

        if not y == self.currY:
            self.move_y(y-self.currY)

        if not z == self.currZ:
            self.move_z(z-self.currZ)




    def move_to_preset_and_measure(self, num_measurements=2):
    # Move to a fixed preset position and take 1-2 measurements.
    # Change these to  desired target position (mm)
        preset_x = 105
        preset_y = 65
        preset_z = 76

        # Clamp to 1 or 2 measurements
        try:
            num_measurements = int(num_measurements)
        except Exception:
            num_measurements = 2
        num_measurements = max(1, min(num_measurements, 2))

        # Home if needed
        if (not self.isHomed.is_set()) or self.stop.is_set():
            self.home_all()

        # Move to preset position
        self.go_to(x=preset_x, y=preset_y, z=preset_z)

        # Optional autofocus before measuring
        self.auto_focus()

        results = []

        for i in range(num_measurements):
            if self.stop.is_set():
                self.resetIdle.set()
                break

            img = self.cam.get_image_array(updateImage=False)
            focus_score = self.cam.calculate_focus_score(imageArray=img)

            results.append({
                "index": i,
                "focus_score": float(focus_score),
                "x_mm": float(self.get_curr_pos_mm("x")),
                "y_mm": float(self.get_curr_pos_mm("y")),
                "z_mm": float(self.get_curr_pos_mm("z")),
            })
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

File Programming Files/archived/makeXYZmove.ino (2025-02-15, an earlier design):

const int enPin=8;
const int stepXPin = 2; //X.STEP
const int dirXPin = 5; // X.DIR
const int stepYPin = 3; //Y.STEP
const int dirYPin = 6; // Y.DIR
const int stepZPin = 4; //Z.STEP
const int dirZPin = 7; // Z.DIR

int stepPin=stepXPin;
int dirPin=dirXPin;

const int stepsPerRev=200;
int pulseWidthMicros = 100;  // microseconds
int millisBtwnSteps = 1000;

void setup() {
  Serial.begin(9600);
  pinMode(enPin, OUTPUT);
  digitalWrite(enPin, LOW);
  pinMode(stepXPin, OUTPUT);
  pinMode(dirXPin, OUTPUT);
  pinMode(stepYPin, OUTPUT);
  pinMode(dirYPin, OUTPUT);
  pinMode(stepZPin, OUTPUT);
  pinMode(dirZPin, OUTPUT);
 
  Serial.println(F("CNC Shield Initialized"));
}

void loop() {
  Serial.println(F("Step 1"));
  makeZMove(0.01);
  delay(500);
//  Serial.println(F("Step 2"));
//  makeZMove(-5);
//  delay(5000);
  
}

void makeMove(double deltaX, double deltaY){

  double deltaA = deltaX + deltaY;
  double deltaB = deltaX - deltaY;


  int stepsA = abs(round(deltaA/0.212058));
  int stepsB = abs(round(deltaB/0.212058));

  
  if (deltaA >= 0){
    digitalWrite(dirXPin, HIGH);
  }
  else{
    digitalWrite(dirXPin, LOW);
  }
  if (deltaB >= 0){
    digitalWrite(dirZPin, HIGH);
  }
  else{
    digitalWrite(dirZPin, LOW);
  }
  for (int i = 0; i < stepsA; i++) {
    digitalWrite(stepXPin, HIGH);
    digitalWrite(stepZPin, HIGH);
    delayMicroseconds(pulseWidthMicros);
    digitalWrite(stepXPin, LOW);
    digitalWrite(stepZPin, LOW);
    delayMicroseconds(millisBtwnSteps);
  }
  
}

void makeZMove(double deltaZ){



  int stepsZ = abs(round(deltaZ/0.01));
  

  if (deltaZ >= 0){
    digitalWrite(dirZPin, HIGH);
  }
  else{
    digitalWrite(dirZPin, LOW);
  }
  for (int i = 0; i < stepsZ; i++) {
    digitalWrite(stepZPin, HIGH);
    delayMicroseconds(pulseWidthMicros);
    digitalWrite(stepZPin, LOW);
    delayMicroseconds(millisBtwnSteps);
  }
  
}

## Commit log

2025-02-25 Add files via upload
    Added housing STL files
    [Housing Base.STL, Housing Top.STL]
2025-02-25 Update readme.md
    Modified read file to have housing base and top
2025-02-27 Update readme.md
    Made note of printing settings for linear rail jigs.
2025-03-01 Delete BOM/OpticalModule_BOM.xlsx
    Deleting old BOM
    [OpticalModule_BOM.xlsx]
2025-03-09 Update readme.md
    Added cable management clips
2025-03-15 Add files via upload
    File for communicating between PC and raspberry pi. This is test raspberry pi file.
2025-03-16 Added initial scanning and RS pages, updated the sample parameters window
2025-03-22 Added some scanning functionality, image tab, and changed enter new samples window
2025-03-23 thread locking
2025-03-23 further updates to thread locking
2025-03-24 calibration exe
2025-03-24 modify random sampling frame
2025-03-24 modified random sampling frame
2025-03-24 disable stepper motor functionality
2025-03-25 removed refresh button, connected sample data
2025-03-30 Add files via upload
    modified and new stl files
    [Belt Tensioner.STL, EnclosureBaseV2.STL, EnclosureCoverFront.STL, EnclosureCoverUpper.STL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]
2025-04-09 ensure in idle before sending sample data
2025-04-09 Update Github BOM.xlsx
    [Github BOM.xlsx]
